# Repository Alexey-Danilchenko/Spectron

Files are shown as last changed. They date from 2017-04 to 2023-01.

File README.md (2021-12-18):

# Spectron

Spectron - an open source project for measuring and obtaining digital devices spectral sensitivity curves

Copyright (C) 2014-Now [Alexey Danilchenko](mailto:alexey.danilchenko@gmail.com), [Iliah Borg](mailto:iliah.i.borg@gmail.com)

*This is a work in progress*

# Introduction

This is the second generation of the open source Spectron project.  Initially this was conceived with the goal of constructing an automated device with an aid to accurately measure spectral sensitivity curves for digital camera sensors. The project has a broader use though and can be used to measure spectral sensitivity curves of various light sensitive sensors (not just camera sensors) - for example spectral sensitivity curves of photodiodes.

The main goal however is still to aid measurement of spectral sensitivity of digital cameras sensors and this is what this project and documentation will be aimed towards. For more details on the application of that and the ultimate reasons _why_ please [read this](CameraSRF.md).

The second generation of Spectron board was produced with the more accurate spectral readings in mind, better analogue circuitry to drive Hamamatsu spectrometers and more stable measurement results.

# Concept

The spectral sensitivity measurements of a selected device are fairly simple in principle:

1. broadband light source of high intensity is passed via monochromator
2. monochromator output is fed to the integrating sphere 
3. integrating sphere output is simultaneously captured by target device and measured spectrally
4. steps 1-3 repeated through selected spectral range in discrete steps (5nm steps over 380-720nm range for example)
5. the results of measurements from target device are scaled accodringly to the spectra of the light measured at each step and target spectral sensitivity curves are produced

# Hardware

The hardware for the above concept consists of the light source (LED or pulsed  Xenon), Mini-Chrom MC1-02 monochromator, 2.5" integrating sphere and several distinct components. The Spectrometer component is a hardware driving Hamamatsu [C12666MA](http://www.hamamatsu.com/jp/en/C12666MA.html) or [C12880MA](http://www.hamamatsu.com/jp/en/C12880MA.html) spectrometer sensor to capture spectral readings from the integrating sphere and initiate synchronised readings from target device. The Stepper Motors component is a hardware for automating monochromator operation (esentially converting manually controlled monochromator to scanning monochromator, turning broadband light source into tunable source). The Light Source component is a hardware for controlling broadband light source that provides input for the monochromator.

With the precise intensity control of the LED light source, the whole system is essentially providing tunable monochromatic light source covering the entire visible range.

All hardware component boards use [Particle Photon controllers](https://docs.particle.io/datasheets/wi-fi/photon-datasheet/) at their core to drive the functionality. Overall application control is performed from Windows/Mac application running on a computer operating the boards via Particle or local cloud (the latter is more responsive).

Boards used for all individual components can be of course utilised for standalone projects - see corresponding sections for details.

For more details please refer to individual parts of the project below:

* [Firmware](firmware) - [Particle Photon](https://www.particle.io/products/hardware/photon-wifi-dev-kit) code running on the boards
* [Hardware](hardware) - boards, schematics (Eagle) and BOM 
* [Software](software) - Windows/MacOS X application controlling the overall functionality

# Open Source

This project is open source software and hardware and is released under:

* [GNU General Public License v3](https://www.gnu.org/licenses/gpl-3.0.en.html) for the software parts and 
* [CERN Open Hardware Licence]( http://www.ohwr.org/attachments/735/CERNOHLv1_1.txt) for hardware parts

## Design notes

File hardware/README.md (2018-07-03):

# Hardware

All the custom made circuits and boards were designed in [Cadsoft Eagle](http://www.autodesk.com/products/eagle/overview). All components for these were separated into standalone Eagle library for easier access. 

__Note:__ All the boards were tuned up for making with [OSH Park](https://oshpark.com/) - all relevant DRC and ERC rule checks were therefore applied an validated.

This project has the following several distinct and standalone components:

* [Spectrometer](Spectrometer) - board controlling spectrometer and performing spectral measurements
* [Stepper Motor Control](Motor) - board driving stepper motor for automating monochromator operation
* [Light Sources](Light_Source) - selection of controllable light sources providing input for monochromator

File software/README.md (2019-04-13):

# Software

*Whilst the Spectron software is being developed and not available yet, I am releasing sample Spectrometer Application here*. 

The SpectrometerApp can operate Spectron board with Hamamatsu C12666 or C12880 sensors remotely via Particle cloud and fully control the Spectrometer operational parameters. The application exercise all Spectrometer board functionality including automatic exposure methods.

The SpectrometerApp allows to use, control and setup the following properties of the Hamamatsu spectrometers:

* Full set of parameters affecting measurement (ADC reference, gain)
* Automatic measurement
* Calculation of CCT, x, y colour metrics for emissive measurements
* Setting/limiting spectrometer range
* Calibration of saturation voltages
* Calibration of black levels
* Correction of spectral response curve

Sample screenshots:

Calibration page for Hamamatsu C12666MA spectrometer with spectral response normalisation curve:

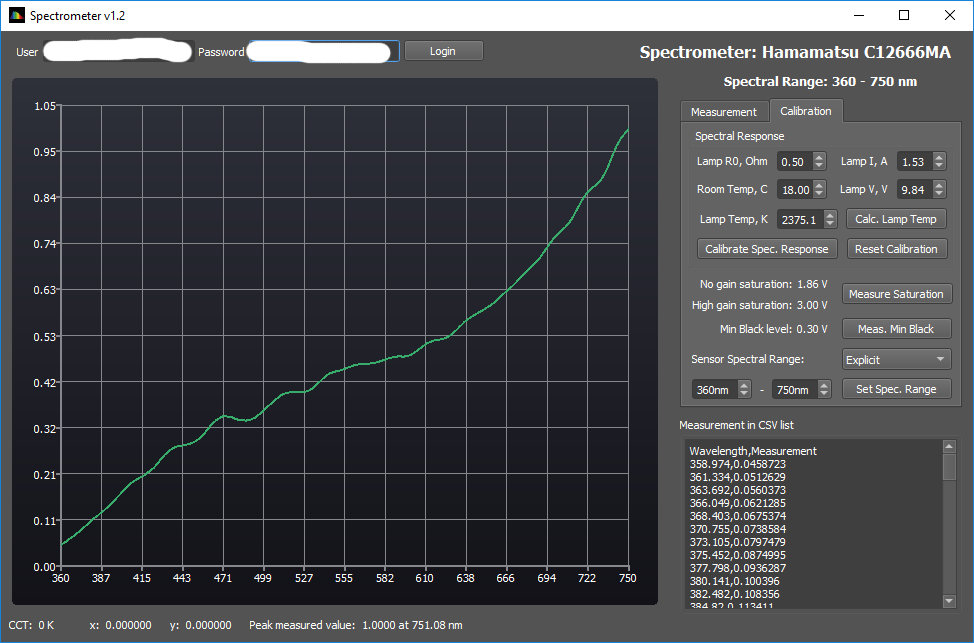
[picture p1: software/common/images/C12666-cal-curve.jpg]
C1266-Cal
 

Automatic measurement of the incandescent lamp (spectrally normalised response) for Hamamatsu C12666MA spectrometer:

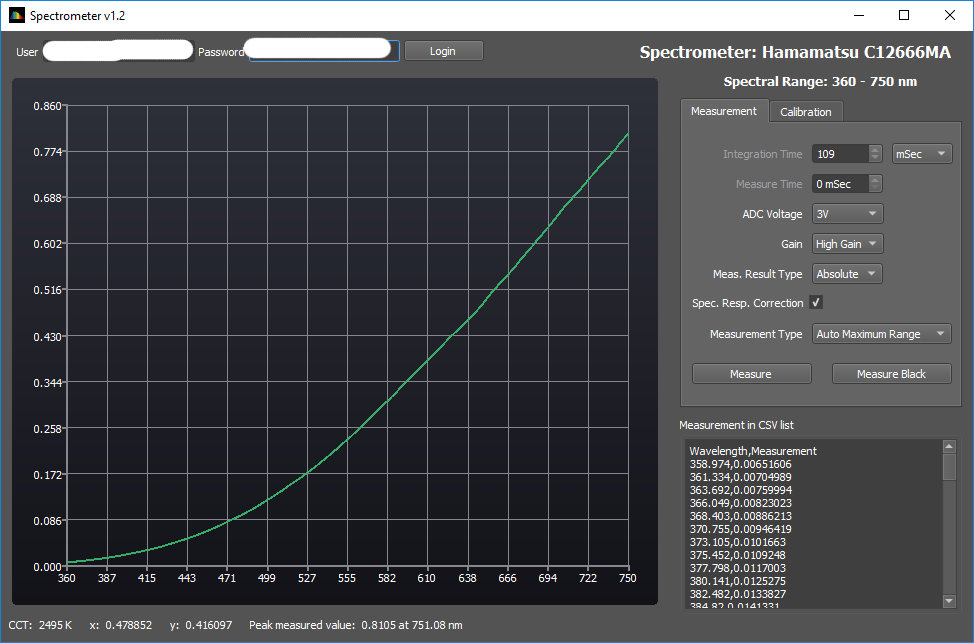
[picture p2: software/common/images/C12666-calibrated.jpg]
C1266-Cal-Meas
 

Automatic raw measurement of the incandescent lamp (no spectral normalisation applied) for Hamamatsu C12666MA spectrometer:

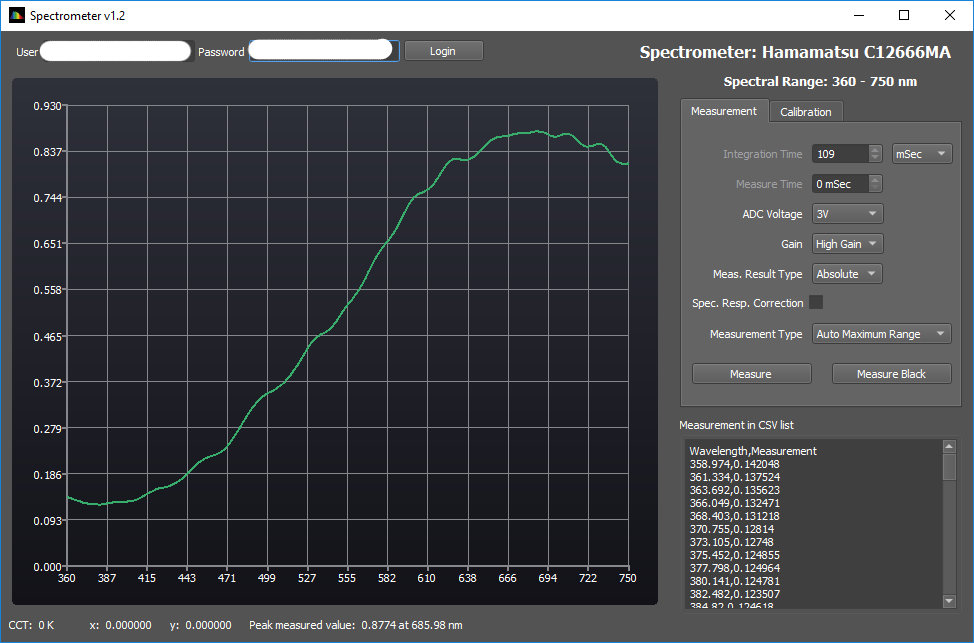
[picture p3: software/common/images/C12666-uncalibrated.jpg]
C1266-Uncal-Meas
 

The SpectrometerApp is written using QT 5.10 with project files are binaries provided for Windows 64 bit platform. It should be fairly easy to compile this on Linux or MacOS platform.

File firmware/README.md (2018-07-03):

# Firmware

This contains all the firmware (and extra example) running on the hardware boards used in this project.

All main board components (Hamamatsu [C12666MA](http://www.hamamatsu.com/jp/en/C12666MA.html), [C12880MA](http://www.hamamatsu.com/jp/en/C12880MA.html) and [TI DRV8884](http://www.ti.com/product/DRV8884)) are implemented as standalone driver objects. This makes it easier to some degree to re-use them on other Particle Photon based projects.

# Spectron 2 Board Fimwares

The main components of the boards are Hamamatsu [C12666MA](http://www.hamamatsu.com/jp/en/C12666MA.html) or [C12880MA](http://www.hamamatsu.com/jp/en/C12880MA.html) spectrometers. Whilst these spectrometer sensors share a lot of common features, operationally they are quite different. A separate firmwares therefore were produced for each spectrometer type.

The spectrometers are driven by hardware timer clock in both cases. The spectrometers readouts are performed via external 16bit SPI based ADC. The board also has four selectable precision voltage references (2.5V, 3.0V, 4.096V and 5V) to allow more precise ADC range fitting to the spectrometer output.

For the purpose of the measurements, the board provides two external trigger pins (only one can be selected and used at a time). The spectrometer driver makes use of the selected trigger pin at the time of the measurement (the trigger signal can be offset and issued prior to the measurement with configurable delay). For the goals of this project, these pins are labelled `TRG_FLASH` and `TRG_CAMERA` in the code for flash and digital camera triggering accordingly.

The spectrometer drivers also have configurable black subtraction mode that could be used to eliminate spectrometer offset voltage (that appears to be nonlinear). This can be configured in one of the following ways:

- to capture black frame output manually 
- to capture black frame output before the main measurement
- to capture black frame output after the main measurement

When black levels are captured the spectrometer readings are adjusted accordingly.

The selected reference voltage, gain (if supported) and black mode are stored in EEPROM and persist even when the board is powered off.

Calibration data provided by Hamamatsu for each sensor (used to determine wavelengths mapping for each sensor) needs to be provided to the driver to get accurate readings. If omitted, the calibration data from my own sensors is used as a fall-back.

All the readings are captured as floating point values in 0..1 range. By default, readings from the driver are also bandpass corrected (this is configurable) using Stearns and Stearns (1988) bandpass correction method.

Below are individual specifics of each firmware.

## Spectron 2 - С12666MA firmware

[This firmware](Spectron_12666) implements the functionality for the Spectron2 board with Hamamatsu [C12666MA](http://www.hamamatsu.com/jp/en/C12666MA.html) spectrometer connected (using appropriate sensor board). 

The spectrometer is driven by hardware clock with 100KHz (default) or 59KHz frequency. In both modes sensor readouts are oversampled to provide more stable readings. The slower clock is enabled by uncommenting `ADC_AVG_4` definition. The specifics of each clock frequency:

* 100KHz: integration times: 11.3msec - 10sec, oversampling with two averaging reads per spectrometer pixel

* 59KHz: integration times: 18.51msec - 10sec, oversampling with four averaging reads per spectrometer pixel

In addition to selectable voltage references, the firmware can enable/disable spectrometer supported gain. This may allow even tighter usage of ADC range.

The firmware is implemented partially outside of Particle Photon HAL - using direct hardware and ports access for performance critical parts (timer, soft pin interrupts, ADC readouts). The readouts are triggered by software pin interrupt - C12666MA (unlike C12880MA) lacks hardware support for signal ready trigger.

## Spectron 2 - С12880MA firmware

[This firmware](Spectron_12880) implements the functionality for the Spectron2 board with Hamamatsu [C12880MA](http://www.hamamatsu.com/jp/en/C12880MA.html) spectrometer connected (using appropriate sensor board). 

The spectrometer is driven by hardware clock with 156KHz (default) or 200KHz frequency. In 156KHz frequency mode sensor readouts are oversampled to provide more stable and smoother readings. The specifics of each clock frequency mode:

* 100KHz: enabled by setting `SPEC_CLK_TICK_TIMER` definition to `SPEC_CLK_156KHZ`, integration times: 345.6usec - 1sec, oversampling with two averaging reads per spectrometer pixel, produces much smoother output, works well even though it is below minimal Hamamatsu specified working frequency

* 200KHz: enabled by setting `SPEC_CLK_TICK_TIMER` definition to `SPEC_CLK_200KHZ`, integration times: 270usec - 1sec, no oversampling with single read per spectrometer pixel, minimal official working frequency for C12880MA according to Hamamatsu specification

The C12880MA does not support gain but is a lot more sensitive than C12666MA. Using selectable reference voltages will allow better use of ADC range.

The firmware is implemented substantially outside of Particle Photon HAL - using direct hardware and ports access for performance critical parts (GPIO pin access, timer, pin interrupts, ADC readouts). The readouts are triggered by C12880MA hardware TRG pin which allows more reliable read timings.

## Spectron 2 - LCD demo firmware

[This firmware](LCD) demonstrates usage of the Spectron 2 board with Hamamatsu C12666MA spectrometer and multipurpose interface connector with [Adafruit 2.2" 18-bit TFT LCD module](https://www.adafruit.com/product/1480) attached. The C12666MA driver should be taken from [C12666 firmware](Spectron_12666) (this avoid the duplication). The firmware will wait for trigger pin (button attached to it) to be risen high, start spectral measurement of predefined integration time and display the spectrum on the TFT screen afterwards.

This code was tested on early stages of the project development but is not actively maintained. Its main purpose if to provide a demonstration of Spectron 2 board capabilities.

# Motor Board Firmware

[This firmware](Motors) implements functionality for the Spectron 2 Motors board that is operating stepper motor and rotary encoder to control monochromator wavelength selection. The [TI DRV8884](http://www.ti.com/product/DRV8884) is used to drive stepper motor and [LS7083](http://www.omnipro.net/lsi-csi/LS7083-S) quadrature converter chip to interface with rotary encoder. 

The DRV8884 allows to fine tune stepper parameters to suit each and every application. All of these stepper parameters as well as position details are stored in EEPROM and persist even when the board is powered off. The expectations are that these particular boards will be tuned up (for example using Particle cloud functions via Particle console) for a specific application and all the board parameters will be set up and stored at that stage.

The firmware is designed to operate in terms of target device position and its lower and upper limits. The logical po
sition is mapped into physical steps for controlling stepper. All position parameters (current position, lower and upper position limits) are also persisted in the EEPROM. For this specific application, current position reflects wavelength selected on monochromator with upper and lower limits designating the spectral range that monochromator can control.

# LED Light Source

[This firmware](LED) implements functionality for Spectron 2 LED Lightsource board using [Yuji VTC 5600K wide spectrum LEDs](https://store.yujiintl.com/collections/vtc-series/products/vtc-series-high-cri-cob-led-135l-pack-5-pcs?variant=45426214099). 

The firmware allows controlling the output brigntness of two LED channels independently (each channel up to 4095 brightness levels) or simultaneously, enabling/disabling LED output as well as doing timed exposures.

It is used as a main light source for Spectron 2 project. 

# Pulsed Xenon Light Source

[This firmware](Xenon) implements functionality for Spectron 2 Xenon Lightsource board using [Excelitas FX-116x series lamps](http://www.excelitas.com/Pages/Product/1100-Series-Family.aspx) on [Excelitas/Perkin-Elmer trigger module FYD‐1150‐B](http://www.excelitas.com/Downloads/DTS_1100Series_Trigger_Modules.pdf) driven by [Excelitas/Perkin-Elmer PS-11xx power supply](http://www.excelitas.com/Downloads/DTS_1100Series_Power_Supplies.pdf). 

The firmware allows controlling the output brigntness (average output power) of the flash lamp, or varying voltage or trigger rate directly (within allowed lamp  specifications), enabling/disabling Xenon Lamp output as well as doing timed exposures.

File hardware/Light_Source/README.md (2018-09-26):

# Light Sources

The Spectron 2 project uses a wideband light source component as an input to the monochromator. Several light sources with full visible spectrum coverage were evaluated, built and tested for this project. It is important to realize that flat spectrum is not necessary in this application. What is required from a light source is continuous spectrum, with no gaps. Evaluated light sources are all satisfy this criteria. Below is the list of the light sources chosen as a result of this evaluation:

* [LED light source](LEDs). _Pros_: great stability and very flexible brightness control, very compact solution electronically. _Cons_: difficult optical constructs required to blend light output from several LEDs into uniform shape suitable as an input for monochromator.

* [Pulsed Xenon short arc light source](Xenon). _Pros_: great visible spectrum coverage, much more even response across spectrum than any other light source solution, compact package and point light source best suited to guide light into the monochromator (very simple construct - essentially lamp against monochromator entrance). _Cons_: expensive if bought from the source (although could be found on eBay at bargain prices), bulky electronics dealing with high voltage triggering (power supplies and trigger modules).

* Tungsten halogen light with regulated power source. _Pros_: the cheapest and readily available solution. _Cons_: needs substantial cooling, needs collimating optics or fiber optical guide to input monochromator, spectrum is the least balanced of all the above solutions (the blue range of the spectrum is weakest), readily available solutions are bulky and external. *NOTE*: This was also tested as readily available light source with fiber optical guide to monochromator and works fine. It is not however considered in details here and mentioned purely due to being very cost effective alternative to the other light sources.

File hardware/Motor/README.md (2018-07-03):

# Motor controller - programmable to scan of a range of wavelengths

This is the board that is responsible for monochromator automation. The board is capable of driving single stepper motor and receiving input from rotary encoder to help with position verification. The board requires minimum +12V DC power supply to operate. The board is also quite useful as standalone Particle Photon stepper driver.

Board schematic is also [available as standalone PDF](Motors.pdf). Bill of material [is available in Excel format](Motors_BOM.xlsx).

The following are the board layouts available (generated by OSH Park preview):

* Spectron 2 Motors - front and back

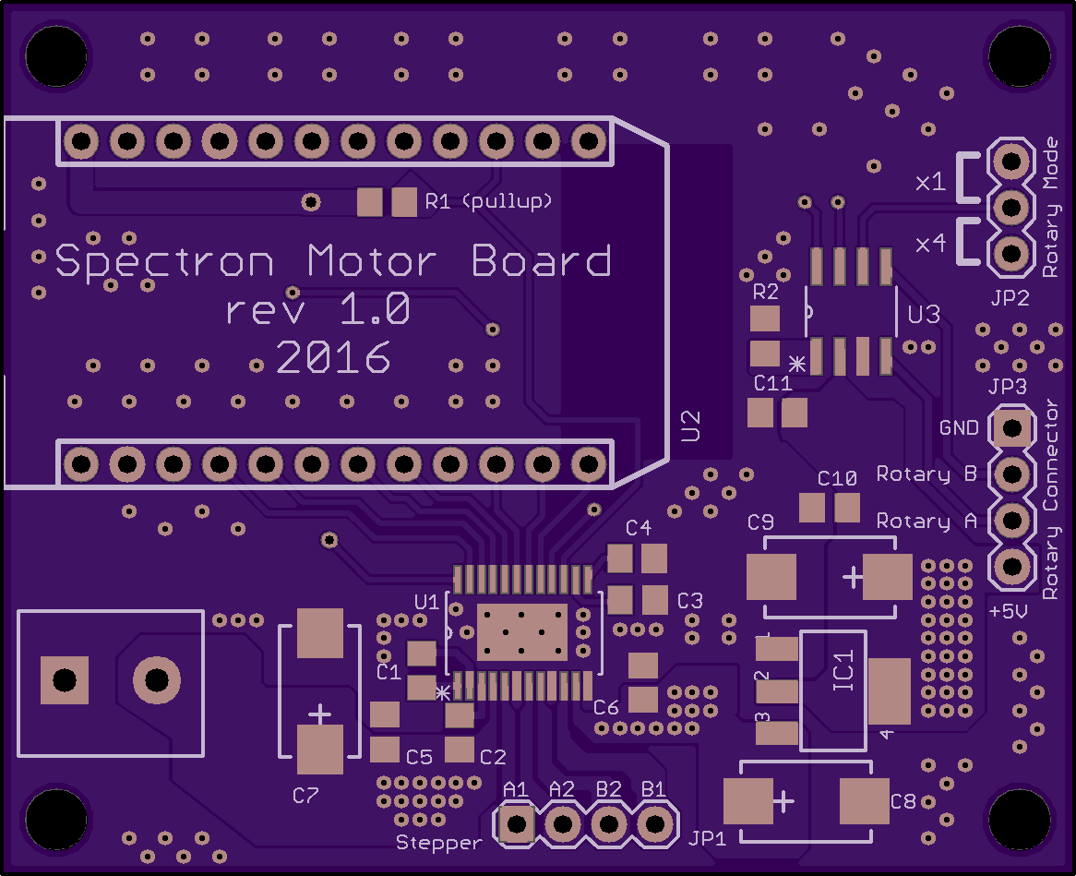
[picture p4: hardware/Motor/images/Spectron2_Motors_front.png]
MOTF
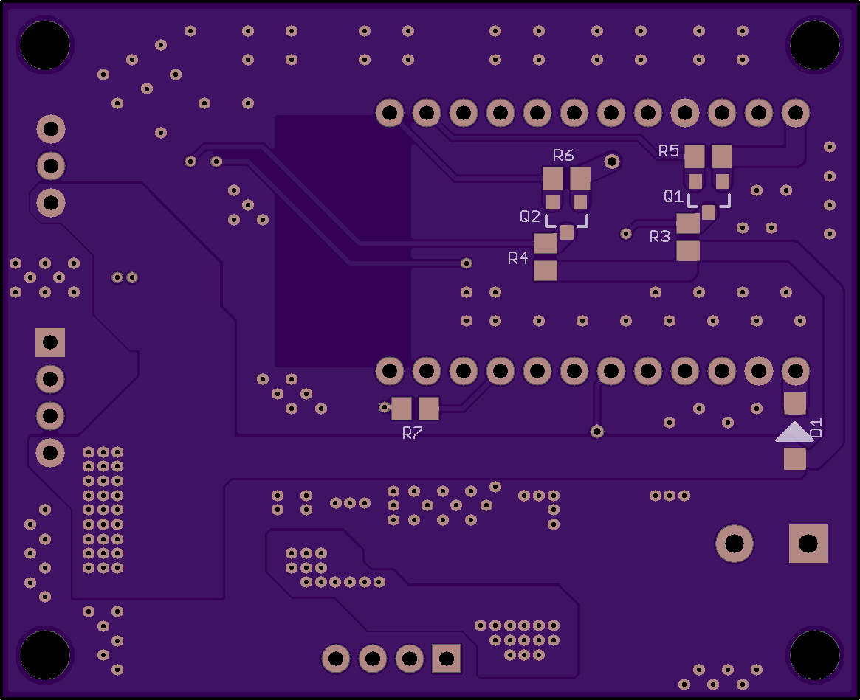
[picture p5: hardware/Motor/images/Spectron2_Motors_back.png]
MOTB


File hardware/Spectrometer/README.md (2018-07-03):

# Spectron 2 - Spectrometer controlling board

This is the main board that is responsible for spectral measurements. The board has analogue circuitry to drive Hamamatsu [C12666MA](http://www.hamamatsu.com/jp/en/C12666MA.html) or [C12880MA](http://www.hamamatsu.com/jp/en/C12880MA.html) micro spectrometers and interfaces to trigger external devices or light sources simultaneously with measurements. The board requires +5V DC power supply to operate.

The board also has a multipurpouse interface connector suitable for custom adaptations that provides access to SPI, I2C and generic digital/analogue pins on Particle Photon. This project does not make use of this connector but example firmware is provided to demonstrate its use with Adafruit 2.2" 18-bit TFT LCD module.

Board schematic is also [available as standalone PDF](Spectron2.pdf). Bill of material [is available in Excel format](Spectron2_BOM.xlsx).

The Hamamatsu C12666MA and C12880MA spectrometers have different hardware pinout and for that reason they are attached to this board through their own little sensor boards. Those were designed with my specific attachment to integrating sphere in mind and come in both vertical and horisontal layouts (they differ in a way the main board attaches to the sensor board).

The following are the board layouts available (generated by OSH Park preview):

* Spectron 2 - front and back

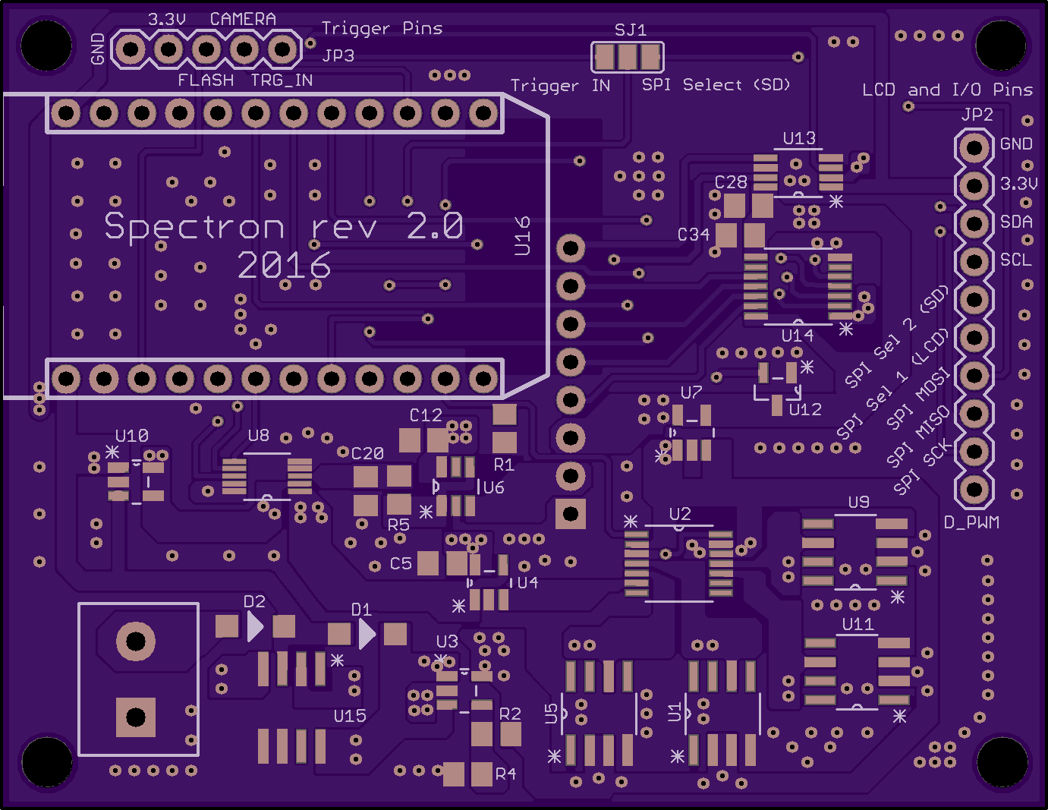
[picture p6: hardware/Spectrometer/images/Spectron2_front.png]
SF
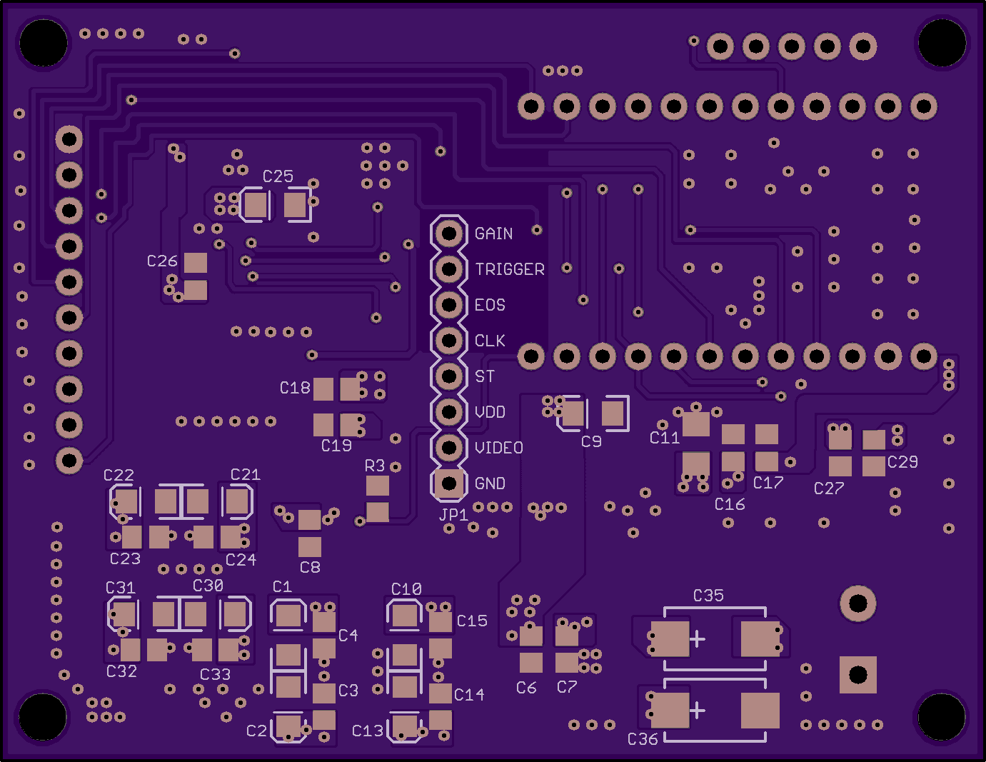
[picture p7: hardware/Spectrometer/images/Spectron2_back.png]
SB
 

* Hamamatsu C12666 sensor board (horisontal) - front and back

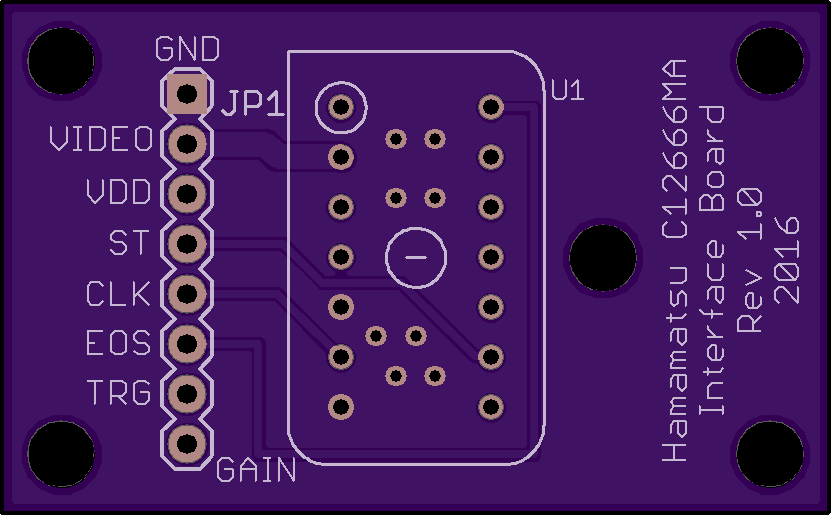
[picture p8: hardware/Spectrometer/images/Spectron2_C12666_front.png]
SF1266
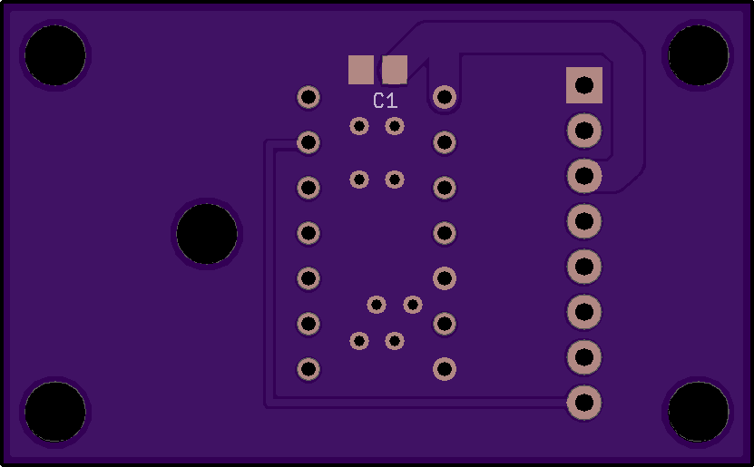
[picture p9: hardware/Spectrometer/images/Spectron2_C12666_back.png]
SB1266
 

* Hamamatsu C12666 sensor board (vertical) - front and back

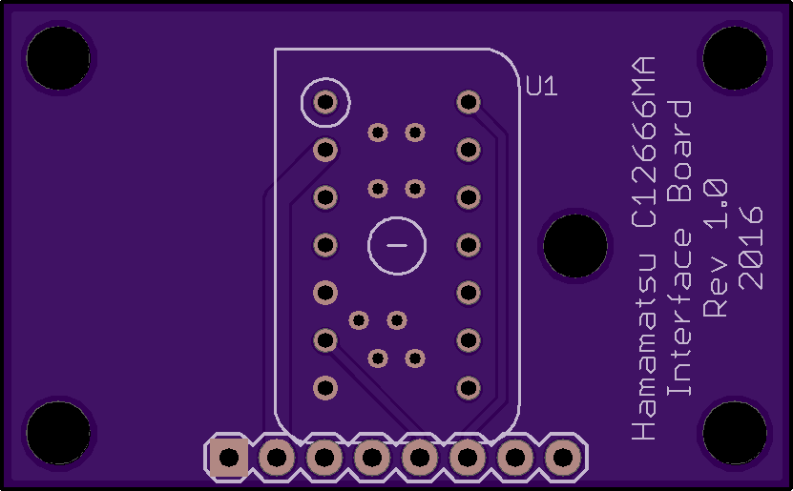
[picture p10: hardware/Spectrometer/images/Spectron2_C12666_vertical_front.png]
SFV1266
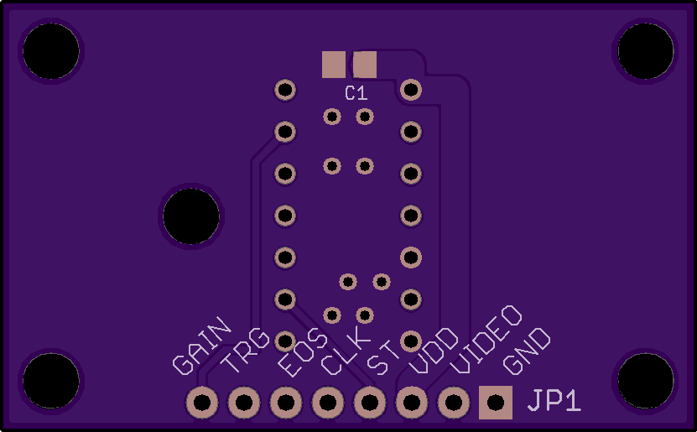
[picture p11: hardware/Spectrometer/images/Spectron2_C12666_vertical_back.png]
SBV1266
 

* Hamamatsu C12880 sensor board (horisontal) - front and back

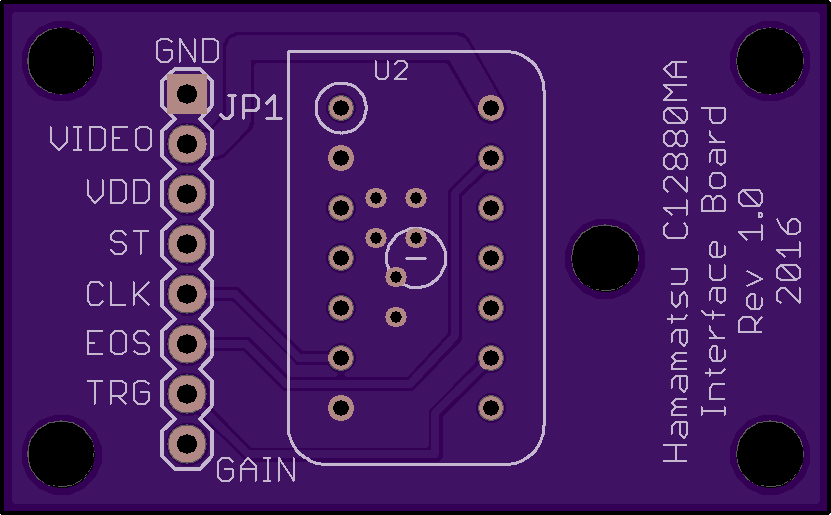
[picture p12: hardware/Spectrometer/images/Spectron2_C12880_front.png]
SF1288
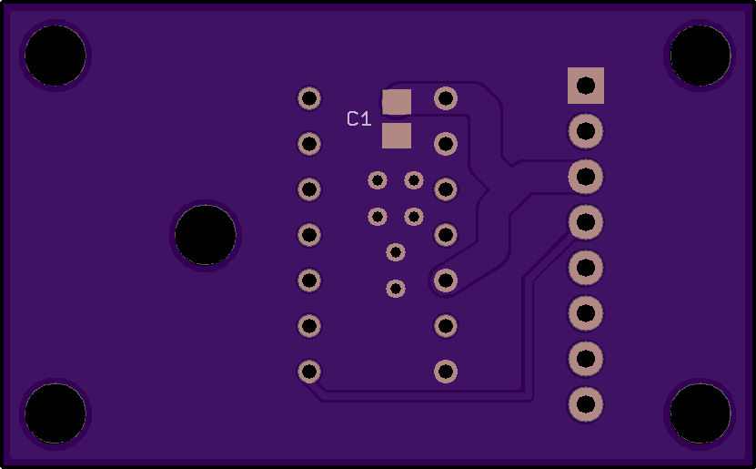
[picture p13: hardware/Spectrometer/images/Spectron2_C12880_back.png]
SB1288
 

* Hamamatsu C12880 sensor board (vertical) - front and back

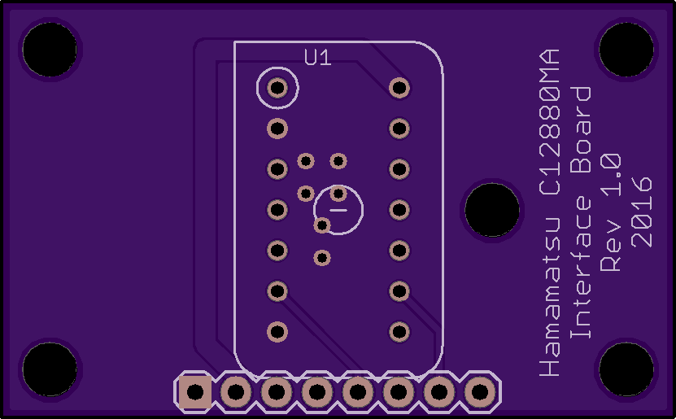
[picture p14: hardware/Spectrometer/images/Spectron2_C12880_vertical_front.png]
SFV1288
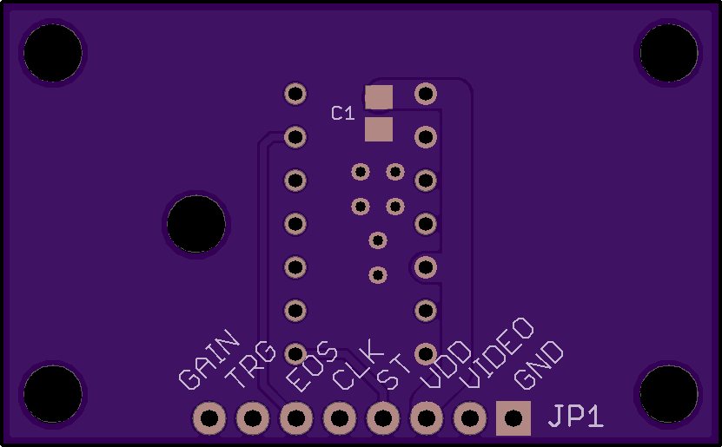
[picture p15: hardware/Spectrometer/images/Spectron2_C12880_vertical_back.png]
SBV1288


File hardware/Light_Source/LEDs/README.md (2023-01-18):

# LED Light Source

The LED light source component uses [Yuji LEDs](https://store.yujiintl.com/). More specifically their VTC (CRI 98) LEDs in [COB package for 5600K](YJWJ040-1.0_YJ-VTC-135L-G01.pdf) correlated colour temperature. A package of 4xVTC LED COBs clustered together is used for this light source. For more technical details on individual COB specifications see [Yuji LED web store](https://store.yujiintl.com/collections/led-cobs/products/yujileds-cri-98-9w-cob-led-135l).

These LEDs were chosen for the broad spectrum coverage they provide. An example of spectral response captured from the LEDs used in this setup ([also available as .CSV file](VTC5600_spectrum.csv)):

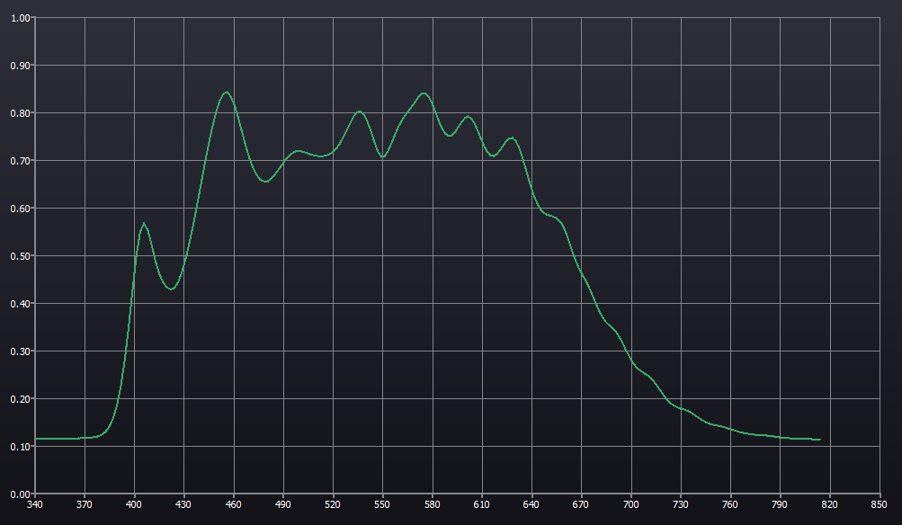
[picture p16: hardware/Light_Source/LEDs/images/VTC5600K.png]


This component consists of two distinct and connected parts - LED driver/controller board and LED light head assembly. The whole circuit requires +12V/5A DC power supply to operate.

The photo below gives a clearer idea of the asssembled setup:

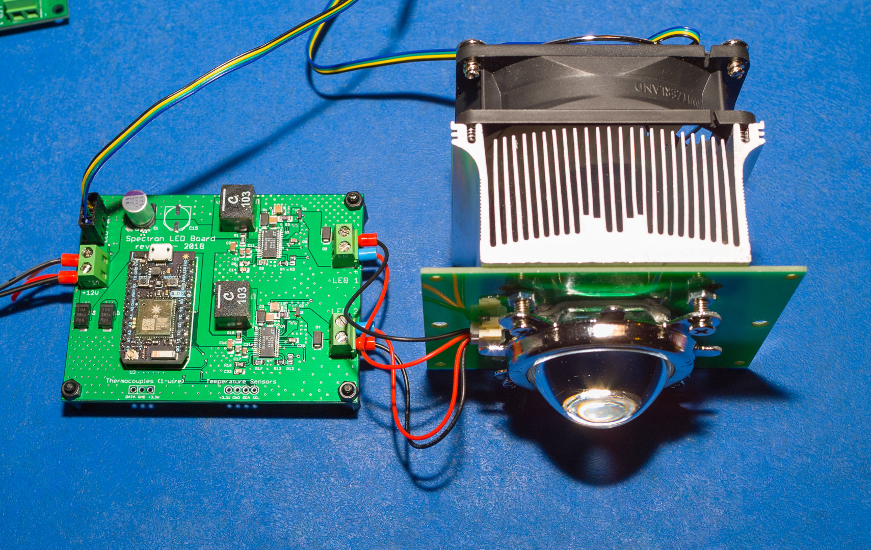
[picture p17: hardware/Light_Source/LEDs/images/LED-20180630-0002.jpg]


### LED Driver Board

The LED driver/controller board is a standalone LED driver with PWM control and 4000:1 dimming ratios (programmatically controlled). The LED driver board has two constant current channels - each capable of driving 450mA LEDs with up to 50V. This setup uses 2x LED strings (one per each channels) with 2xLEDs in series in each string (4x LEDs in total).

The board has 4 pin PWM connector allowing to control LED heatsink fan (if it is used). It also features I2C temperature sensor connector for board/environment temperature monitoring (if used) and 1-Wire thermocouple interface connector for LED temperature monitoring (if used).

Board schematic is also [available as standalone PDF](LED.pdf). Bill of material [is available in Excel format](LED_BOM.xlsx).

The following are the board layouts available (generated by OSH Park preview):

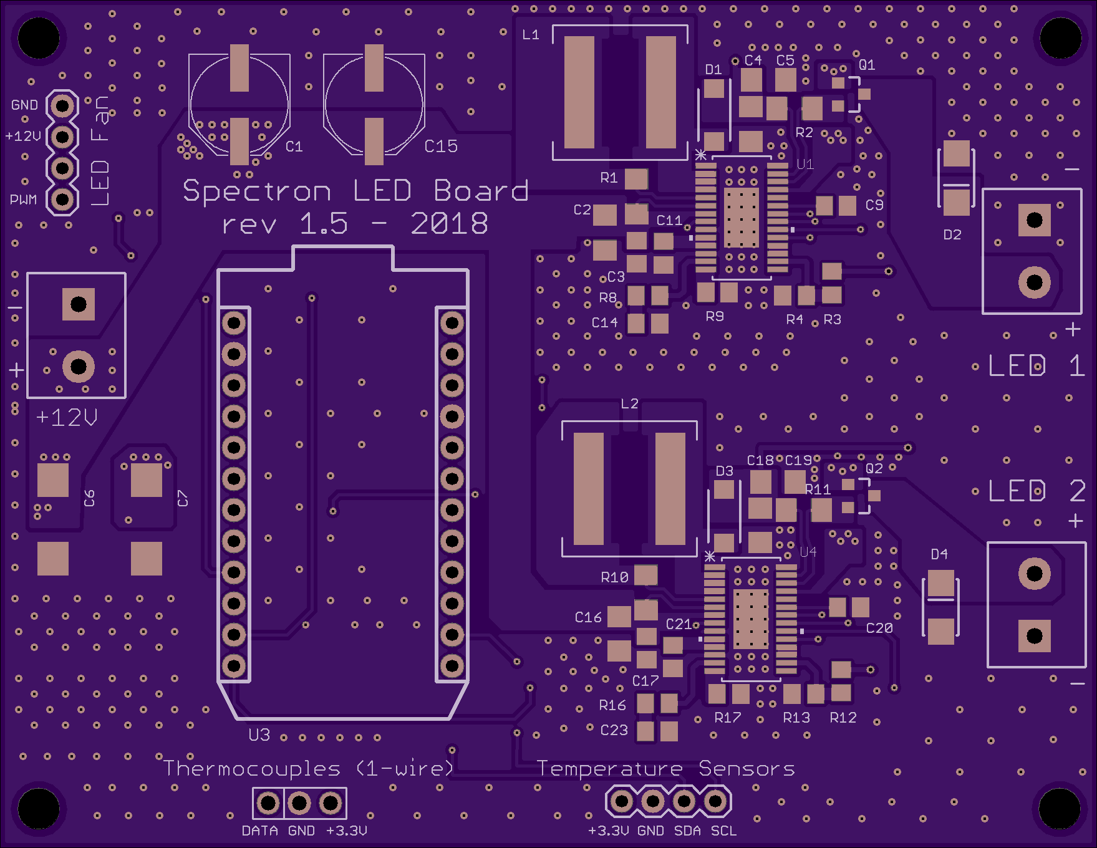
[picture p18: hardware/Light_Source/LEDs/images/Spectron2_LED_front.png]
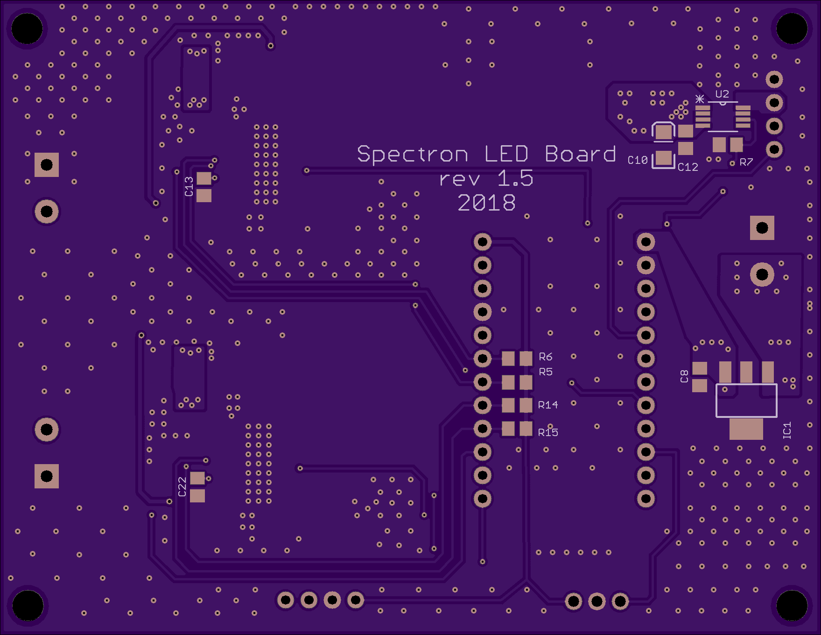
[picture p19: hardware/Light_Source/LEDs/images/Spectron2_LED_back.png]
SB
 

### LED Light Head Assembly

This assembly utilises the board with connector to the main LED driver board and mechanical connectors to 4xVTC LED COBs mounted directly on heatsink. The board has square cutout that fits tightly around 2x2 layout of VTC LED COBs with metallic pins soldered to the board acting as mechanical connectors to the LEDs. This allows to keep LEDs and heatsink setup separate from the board and optical assembly for easier replacement of the parts. The LED COBs are connected in series of two per string. 

The LED COBs are glued to a heatsink directly with [Arctic Silver Thermal Adhesive](http://www.arcticsilver.com/arctic_silver_thermal_adhesive.htm) in a tightly formed cluster. In series connection for each pair is formed by direct wire soldering onto the LEDs. This photo illustrates the setup:

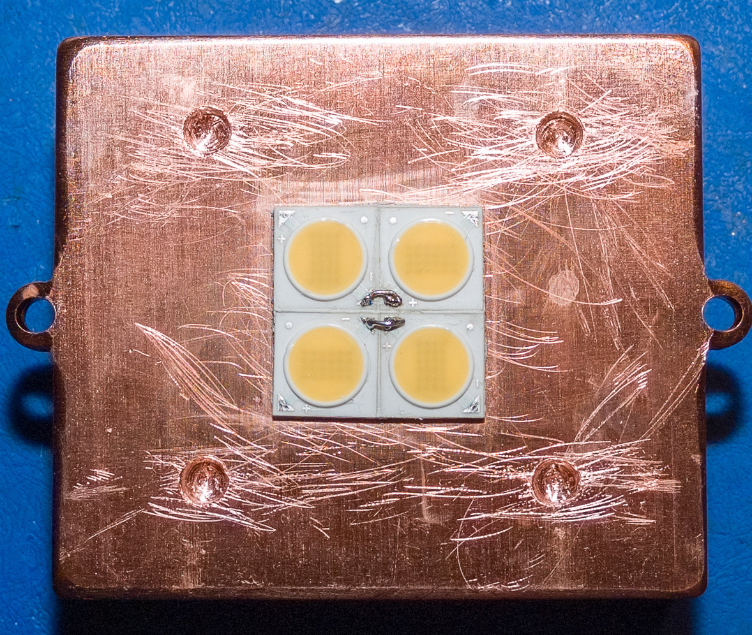
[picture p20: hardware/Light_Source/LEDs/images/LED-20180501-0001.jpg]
 

The board with soldered pins on top of LEDs mounted on heatsink as follows:

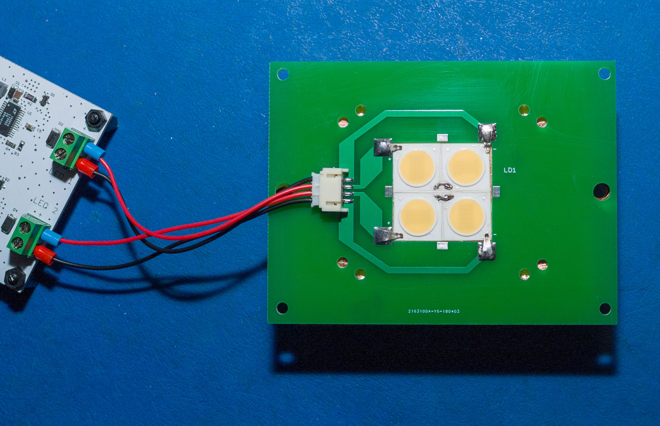
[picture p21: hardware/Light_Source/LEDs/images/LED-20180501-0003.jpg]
 

The board then has a range of holes to allow attachments of the reflector, condenser lens and holder. Below is the example of the fully assembled setup:

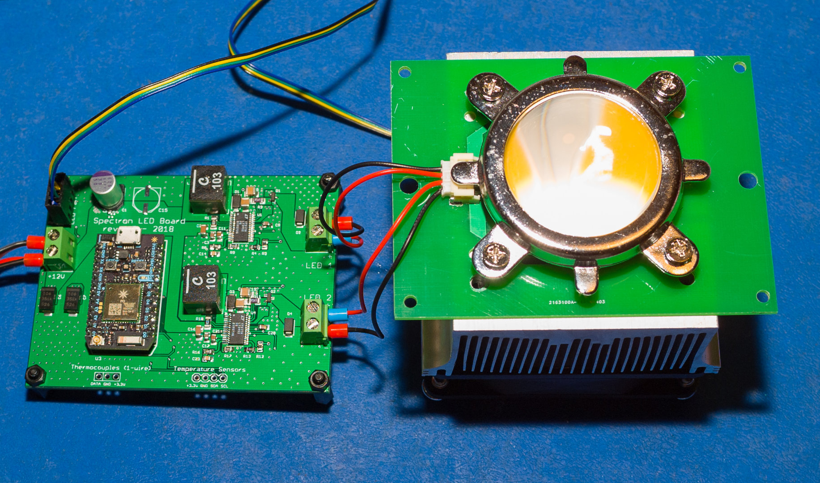
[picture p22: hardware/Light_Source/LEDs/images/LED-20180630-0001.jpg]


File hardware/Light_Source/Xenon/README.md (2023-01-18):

# Xenon Light Source

The Xenon light source component utilises compact pulsed guided short arc Xenon lamp with build in reflector. There are several manufacturers of those lamps - [Hamamatsu](https://www.hamamatsu.com/jp/en/product/light-and-radiation-sources/lamp/xe-f.html) and [Excelitas/Perkin-Elmer](https://www.excelitas.com/product/1100-series-short-arc-xenon-lamps) are well known for their expertise in this area. The setup built and tested for the Spectron 2 utilises [Excelitas/Perkin-Elmer](http://www.excelitas.com/) lamps simply because the off-the-shelf components for them are much easier to find reasonably priced on second hand market (eBay is a great source for them).

This light source construction makes it a very efficient light source for monochromator with very little light loss even without special complicated collimating optics. The metal can lamps from the families referenced above also allow to exceed to a certain degree rated power parameters when lamp is mounted on cooling jackets with sufficient thermal mass. This was tested and fully exploited in firmware accompanying this light sources to provide more efficient light output.

This light source uses [Excelitas/Perkin-Elmer FX-1160 (arc length 1.5mm) or FX-1163 (arc length 3mm) lamps](hhttps://www.excelitas.com/product/1100-series-short-arc-xenon-lamps) widely available new on [eBay at reasonable prices](https://www.ebay.com/itm/Excelitas-FX-1163RT-High-Output-Short-Arc-Xenon-Flashlamp-Flashtube-New-in-Box/122220610629). The lamp also needs a corresponding high voltage (400-1000V) power supply and high voltage trigger module. In our case the [Excelitas/Perkin-Elmer PS-1120 high voltage power supply](http://www.excelitas.com/Downloads/DTS_1100Series_Power_Supplies.pdf) was used together with [Excelitas/Perkin-Elmer FYD‐1150‐B high voltage trigger module](http://www.excelitas.com/Downloads/DTS_1100Series_Trigger_Modules.pdf). The controller board was made to allow to programmatically control the output voltage and triggering rate.

The whole light source component requires external +24V/3A DC power supply to operate.

The pictures below give a clearer idea of the asssembled setup for this component with the lamp triggering:

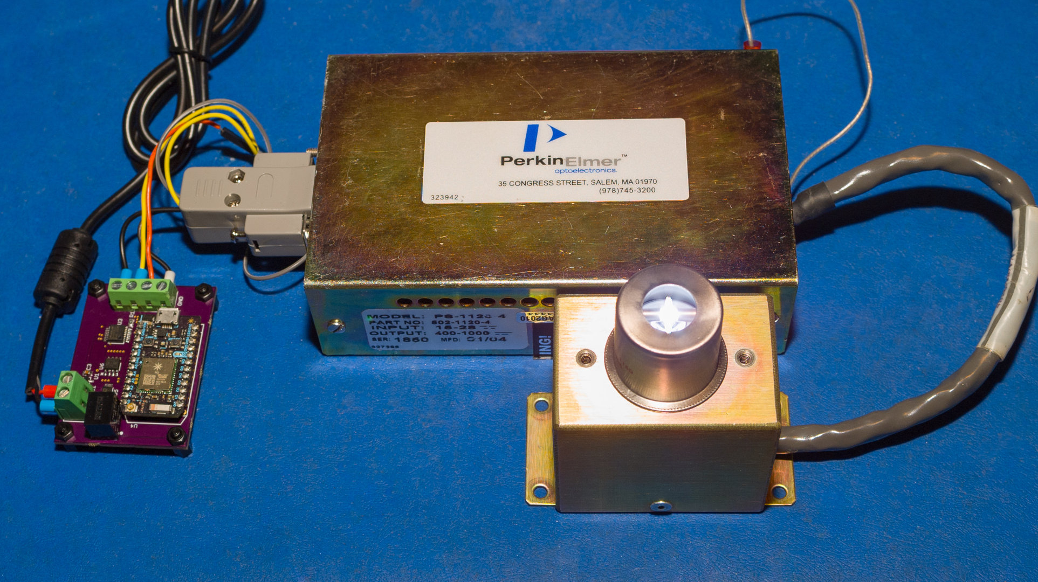
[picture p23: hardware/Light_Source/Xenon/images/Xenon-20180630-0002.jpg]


The controller board uses 0-10V DAC to set output voltage of the high voltage power supply - these power supplies tend to use voltage reference of 1/100th of the desired output to control the output voltage. The board has 2 pin connector to the exnternal +24V DC power supply and 4 pin connector to the high voltage power supply driving the lamp. The output 4 pin connector provides +24V DC, non-isolated logic level trigger signal and 0-10V voltage reference. The [Excelitas/Perkin-Elmer PS-1120 high voltage power supply](http://www.excelitas.com/Downloads/DTS_1100Series_Power_Supplies.pdf) used here has isolated trigger input so no extra isolation is needed. However external trigger signal isolation may be needed (via optocoupler) if a different high voltage power supply is used.

Board schematic is also [available as standalone PDF](Xenon_Light.pdf). Bill of material [is available in Excel format](Xenon_Light_BOM.xlsx).

The following are the board layouts available (generated by OSH Park preview):

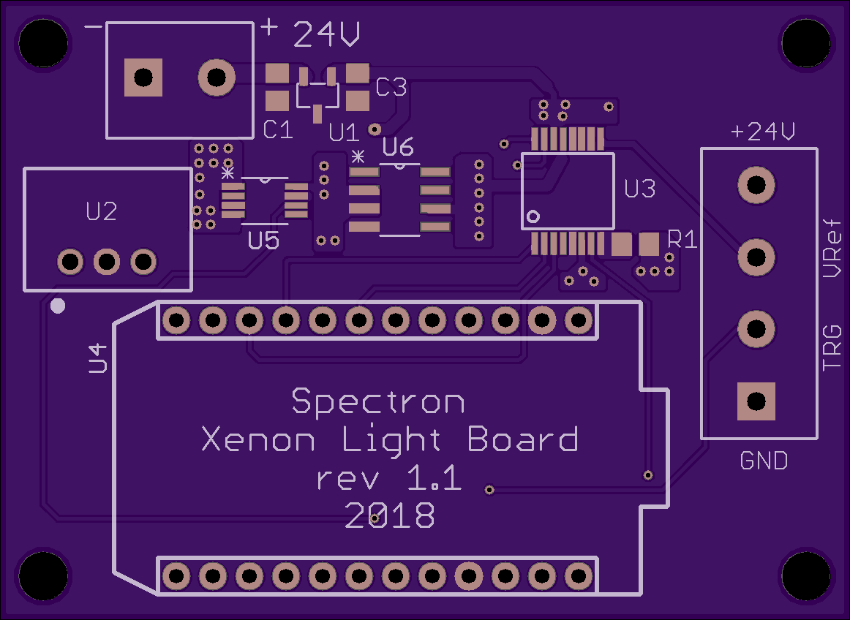
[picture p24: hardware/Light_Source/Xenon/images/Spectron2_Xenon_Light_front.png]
 SB

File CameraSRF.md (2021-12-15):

# Practical application of camera sensor spectral response function

The goal here is to obtain data that would allow us to compute an ad hoc (flexible, actual scene- and light-tailored, adjustable during the raw conversion process) colour transform between raw RGB and perceived colour, based directly on the spectral properties of the light in the scene and the sensor spectral sensitivity.

The popular approach to camera colour profiling is to shoot a target, and, knowing the colours on the target, to compute a transform between those colours and the corresponding values in the digital capture.

Problems with the profiling that is based on shooting a target include:
- minimizing illumination non-uniformity across the target (in terms of intensity / white balance)
- minimizing stray light
- minimizing (colour) reflexes from the surroundings
- minimizing flare and glare introduced by the lighting and the lens
- minimizing lens vignetting
- minimizing digital vignetting / angular dependencies introduced by the sensor
- optimizing exposure to avoid noisy and non-linear areas on the sensor characteristic curves
- minimizing the target reference data uncertainty
- a limited number of patches on the target, and the limited real-world-adequacy of those patches’ spectral distributions
- dependency of the resulting profile on the shooting light spectrum is very problematic, given the diversity of the light sources used for actual shooting
- limited quality and accuracy of chromatic adaptation in a 3D colour domain when attempting to adapt the profile to the light in an actual shot (especially when the actual light sources don't have smooth spectra, like it is with LEDs and fluorescent light sources, or, in general, when the light used to shoot the target and the light in the actual shot are far apart spectrally / CCT-wise)

In summary, profiling based on shooting a target has rather limited applicability as it depends on many factors, some of which are hard / costly to control, while some, mostly the chromatic adaptation, may not be solvable at all.

To overcome these limitations we will be using the basic physical property of the sensor - spectral sensitivity (it has, by the way, its own EXIF tag, 34852 / 0x8824, which we never saw to be used). Spectral sensitivity, measured once, can be used to create colour transforms without any target shots, on the fly, and those transforms can be tailored to the light in an actual shot.

## Terminology

**SPD** - _spectral power distribution_, a graph / histogram (often a table) of wavelengths and corresponding intensities (energy levels). SPD characterizes emitted or reflected light. SPD of the light falling on a sensor / receptor (human eye) causes sensor / receptor excitation.

Sensor excitation results in raw RGB response in the form of raw RGB data.

Eye excitation results in the sensation of colour, that is in human colour perception. Human response can be represented as CIE XYZ. (Actually, we can use the LMS responsivity spectra of human perception instead of XYZ.)

**SRF** - _spectral response function_ (aka spectral sensitivity). Here it is used to predict the sensor raw RGB response when the sensor is excited by a light of the given wavelength falling on it.

SRF for a sensor is much like an observer colour matching functions for human perception; in both cases responses are additive, that is the total response to an SPD falling on the sensor / receptor is the sum of responses to individual pairs 'wavelength - intensity'.

We will use **\<cam observer\>** for SRFs.

## Computation method

To compute a colour transform using an SRF, first we need to define some excitation and determine both the human response (XYZ) and the camera response (raw RGB) for this excitation.

We will be using \<cam observer\> over a simulated excitation SPD in order to obtain a set of raw RGB data. Such simulation offers at least 3 benefits:
- any synthetic calibration target can be used, including targets that are nearly impossible to create physically and shoot; all one needs is spectral measurements of objects - colours in Nature (leaves, flowers, ...), various skin tones, etc. - and now there in no target properties uncertainty or need in exposure optimization;
- since the light is virtual, each synthetic calibration target "patch" is under the same light SPD (no angular dependencies, no intensity variations, no white balance variations, no shading, no colour reflexes from the surroundings, no lens / digital vignetting, etc.);
- we can calculate light-in-the-scene tailored colour transforms "on the fly" by interactively adjusting the light SPD while rendering raw, or using measured light SPD to match the light in the actual photographed scene (instead of applying chromatic adaptation on top of a colour transform or interpolating between the colour transforms in a reduced, compared to spectra, 3D colorimetric space).

### Inputs
- simulated spectral excitation - some set of spectral data that excites the receptors (the sensor and the eye). It can be a product of some reference spectral reflection data and some light SPD, or SPDs of a multitude of coloured lights / filtered lights
- sensor SRF (camera observer)
- the human perception (CIE XYZ data) of that spectral data (to be determined using the standard colorimetry formulae)
- the camera perception (raw RGB) of that spectral data (predicted trough the sensor SRF / camera observer)

### End result
- a colour transform between raw RGB and XYZ colorimetric space, can be a 3x3 matrix, can be something more complex

### Let
- *\<scene light SPD\>* be a known / asserted light in a scene for which we want to calculate the colour transform
- *\<calibration target sd\>* be spectral reflection data of a real / synthetic calibration target
- *\<human observer\>* be the observer used to render \<calibration target sd\> to XYZ

To determine the raw RGB, we will be rendering the sensor excitation through the camera observer.

XYZ (human perception) is:

> *\<calibration target XYZ\>* = *\<scene light SPD\>* * *\<calibration target sd\>* * *\<human observer\>*

From the camera side, with *\<calibration target sd\>* in \[0 .. 1\] domain

> *\<simulated sensor excitation\>* = *\<calibration target sd\>* * *\<scene light SPD\>*

By definition

> *\<sensor excitation\>* * *\<cam observer\>* = *\<raw RGB\>*

Thus

> *\<simulated raw RGB\>* = *\<simulated sensor excitation\>* * *\<cam observer\>*

Having *\<calibration target XYZ\>* and *\<simulated raw RGB\>* we can proceed to calculate a colour transform.

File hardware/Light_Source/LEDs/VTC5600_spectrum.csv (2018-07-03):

Wavelength | Measurement
325.751 | 0.0523601
328.134 | 0.119326
330.515 | 0.115091
332.895 | 0.115171
335.274 | 0.115119
337.652 | 0.115133
340.027 | 0.114955
342.402 | 0.11523
344.774 | 0.115035
347.145 | 0.114638
349.515 | 0.115063
351.882 | 0.115195
354.248 | 0.115177
356.612 | 0.115141
358.974 | 0.115152
361.334 | 0.115265
363.692 | 0.115355
366.049 | 0.11595
368.403 | 0.116141
370.755 | 0.116135
373.105 | 0.116733
375.452 | 0.118325
377.798 | 0.119781
380.141 | 0.123509
382.482 | 0.129645
384.82 | 0.140261
387.156 | 0.158131
389.49 | 0.186038
391.821 | 0.226206
394.15 | 0.280545
396.476 | 0.348927
398.8 | 0.425779
401.121 | 0.498651
403.439 | 0.549225
405.754 | 0.567
408.067 | 0.552515
410.377 | 0.521328
412.684 | 0.487716
414.989 | 0.461417
417.29 | 0.442937
419.588 | 0.43229
421.884 | 0.428162
424.176 | 0.431721
426.466 | 0.444214
428.752 | 0.465883
431.036 | 0.494465
433.316 | 0.528558
435.593 | 0.565869
437.867 | 0.606814
440.137 | 0.648959
442.405 | 0.691133
444.669 | 0.731603
446.929 | 0.768233
449.187 | 0.799734
451.441 | 0.824182
453.691 | 0.839071
455.938 | 0.842363
458.182 | 0.833206
460.422 | 0.814464
462.659 | 0.788699
464.892 | 0.759086
467.121 | 0.730372
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

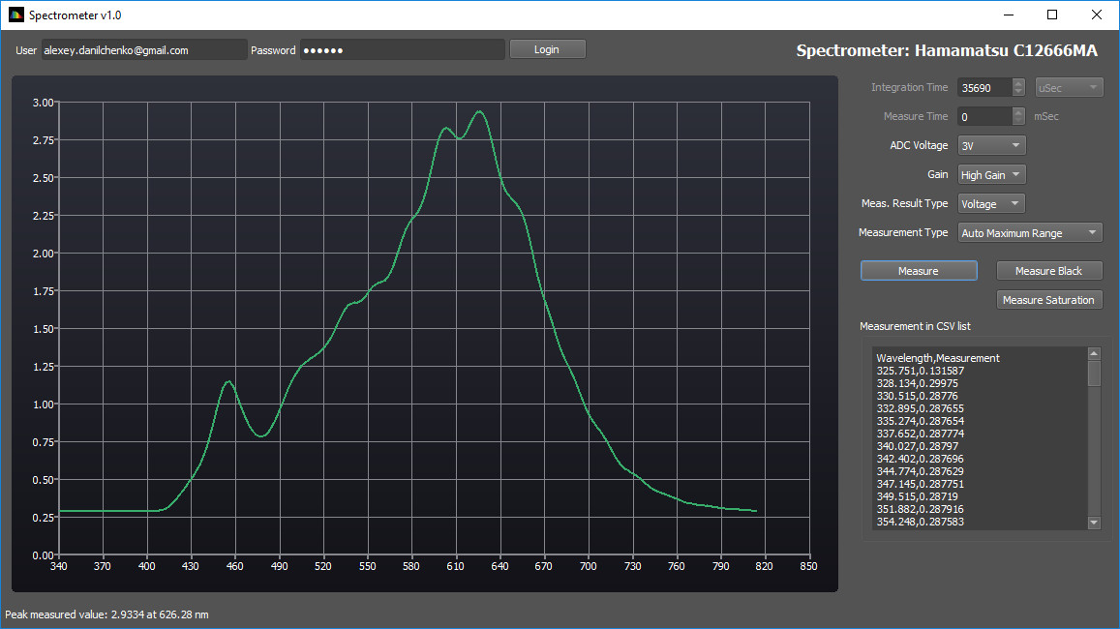
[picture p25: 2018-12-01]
software/common/images/Spectrometer.jpg

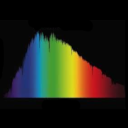
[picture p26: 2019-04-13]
software/common/images/SpectrometerApp.png

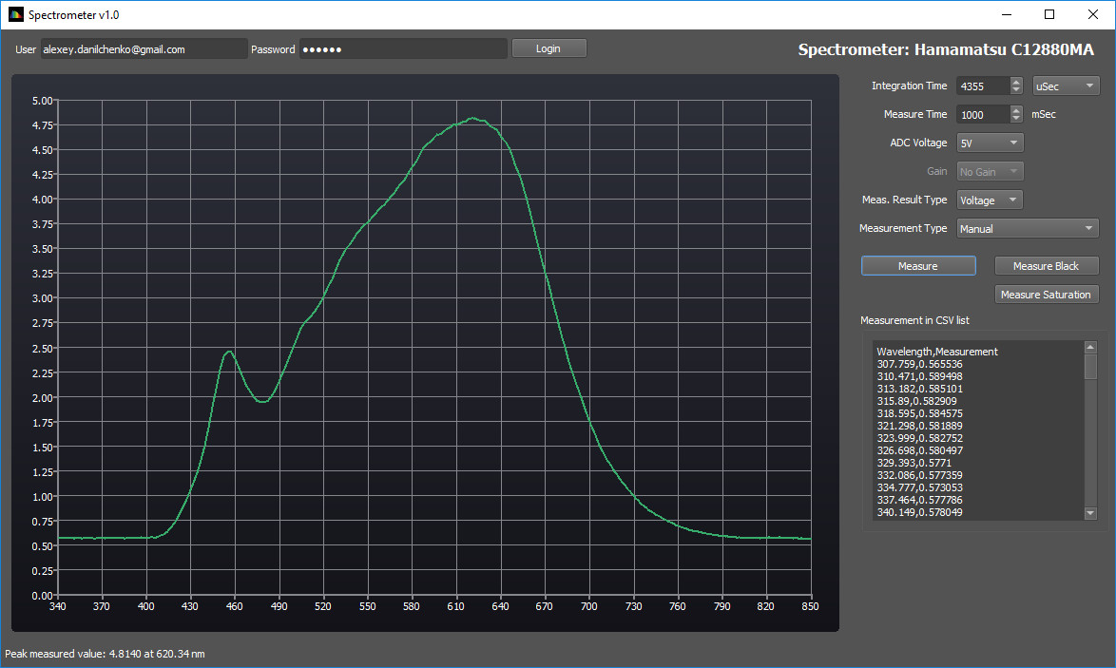
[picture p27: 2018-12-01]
software/common/images/Spectrometer2.jpg

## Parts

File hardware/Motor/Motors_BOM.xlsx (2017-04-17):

Qty | Value | Device | Package | Parts | Description | MPN | SUPPLIER | Distributor | Distributor Part Number
2 | 0.01 uF | C-EUC0805 | C0805 | C5, C6 | Multilayer Ceramic Capacitors MLCC - SMD/SMT 0805 0.01uF 100volts X7R 10% | C2012X7R2A103K085AA | TDK | Mouser | 810-C2012X7R2A103K
1 | 0.022 uF | C-EUC0805 | C0805 | C1 | Multilayer Ceramic Capacitors MLCC - SMD/SMT 0805 100volt 0.022uF X7R 10% Soft Term | GCJ216R72A223KA01D | Murata | Mouser | 81-GCJ216R72A223KA1D
1 | 0.1uF | C-EUC0805 | C0805 | c10, C11 | Multilayer Ceramic Capacitors MLCC - SMD/SMT 0805 0.1uF 25volts X7R 10% | GRM21BR71E104KA01L | Murata | Mouser | 81-GRM40X104K25L
1 | 0.22 uF | C-EUC0805 | C0805 | C2 | Multilayer Ceramic Capacitors MLCC - SMD/SMT 0805 0.22uF 25volts X7R 10% | GRM219R71E224KA01D | Murata | Mouser | 81-GRM21R71E224KA01D
2 | 0.47 uF | C-EUC0805 | C0805 | C3, C4 | Multilayer Ceramic Capacitors MLCC - SMD/SMT 0805 0.47uF 25volts X7R 10% | C2012X7R1E474K125AA | TDK | Mouser | 810-C2012X7R1E474K
1 | 100 K | R-EU_R0805 | R0805 | R2 | Thick Film Resistors - SMD 1/8watt 100Kohms 1% 100ppm | CRCW0805100KFKEA | Vishay | Mouser | 71-CRCW0805-100K-E3
1 | 100uF | CPOL-USCT7343 | CT7343 | C7 | Tantalum Capacitors - Polymer SMD 25volts 100uF 20% ESR=60mohms | T521X107M025ATE060 | Kemet | Mouser | 80-T521X107M25ATE60
4 | 10K | R-EU_R0805 | R0805 | R3, R4, R5, R6 | Thick Film Resistors - SMD 1/8watt 10Kohms 1% 100ppm | CRCW080510K0FKEA | Vishay | Mouser | 71-CRCW0805-10K-E3
1 | 47uF | CPOL-USCT7343 | CT7343 | C8, C9 | Tantalum Capacitors - Polymer SMD 35volts 47uF 20% ESR=30mohms | T521X476M035ATE030 | Kemet | Mouser | 80-T521X476M35ATE30
1 | 5K | R-EU_R0805 | R0805 | R1 | Thick Film Resistors - SMD 1/8watt 5Kohms 1% | CRCW08055K00FKTA | Vishay | Mouser | 71-CRCW0805-5K
2 | BSS138 | MOSFET-NCHANNELSMD | SOT23-3 | Q1, Q2 | MOSFET SOT-23 N-CH LOGIC | BSS138 | Fairchild Semiconductor | Mouser | 512-BSS138
1 | DRV8884PWPR | DRV8884PWPR |  | U1 | Motor/Motion/Ignition Controllers & Drivers 1.0A Stepper Motor Driver With 1/16 Microstepping and Integrated Current Sensing (STEP/DIR Ctrl) 24-HTSSOP -40 to 125 | DRV8884PWPR | Texas Instruments | Mouser | 595-DRV8884PWPR
1 | LS7083N-S | LS7083N-S |  | U3 | CMOS quadrature clock converter | LS7083N-S | LSI/CSI | OmniPro | LS7083N-S
1 | MC33269ST | MC33269ST | SOT223 | IC1 | LDO Voltage Regulators 3.3V ADJ 800mA | MC33269ST-3.3T3G | ON Semiconductor | Mouser | 863-MC33269ST-3.3T3G
1 | PMEG2010ER | DIODE-SOD123 | SOD123 | D1 | Schottky Diodes & Rectifiers SCHOTTKY LOW VF | PMEG2010ER,115 | NXP | Mouser | 771-PMEG2010ER115
1 | POWERSUPPLY_DC21MMX | POWERSUPPLY_DC21MMX | POWERSUPPLY_DC-21MM | DC1 | DC Power Connectors Power Jacks | PJ-102AH | CUI Inc. | Mouser | 490-PJ-102AH
1 | PHOTON | PHOTON Without Headers | PHOTON | U2 | WiFi/802.11 Development Tools Photon no headers | PHNTRAYNOH | Particle
2 | Photon socket | Preci-Dip 714-87-112-31-012101 |  |  |  | 714-87-112-31-012101 | Preci-Dip | DIGIKEY | 1212-1166-ND
2 | Photon headers for the sockets above | Preci-Dip 350-80-112-00-006101 |  |  |  | 350-80-112-00-006101, 350-PP-1NN-00-006101 series | Preci-Dip | RS-Online | 702-0095
1 | Rotary Connector | M04PTH | 1X04 | JP3 | Header 4
1 | Stepper Connector | M04PTH | 1X04 | JP1 | Header 4
1 | X1/X4 Jumper | M03PTH | 1X03 | JP2 | Header 3

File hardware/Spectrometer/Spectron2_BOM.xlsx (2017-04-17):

Qty | Value | Device | Package | Parts | Description | MPN | SUPPLIER | Distributor | Distributor Part Number
4 | 1uF | TANT-CAP1206 | EIA3216 | C1, C10, C21, C30 | Tantalum Capacitors - Solid SMD 1uF 25volts 10% A case Molded | 593D105X9025A2TE3 | Vishay | Mouser | 74-593D105X9025A2TE3
1 | 22uF | C-EUC0805 | C0805 | C11 | Multilayer Ceramic Capacitors MLCC - SMD/SMT 0805 22uF 25volts X5R 20% | GRM21BR61E226ME44L | Murata | Mouser | 81-GRM21BR61E226ME4L
6 | 10uF | C-EUC0805 | C0805 | C6, C7,C18, C19, C27, C29 | Multilayer Ceramic Capacitors MLCC - SMD/SMT 0805 10uF 35volts *Derate Voltage/Temp | GRM21BC71E106KE11L | Murata | Mouser | 81-GRM21BC8YA106KE1L
1 | 2.7 nF | C-EUC0805 | C0805 | C20 | Multilayer Ceramic Capacitors MLCC - SMD/SMT 0805 2700pF 25volt X7R +/-10% | GRM216R71E272KA01D | Murata | Mouser | 81-GRM216R71E272KA1D
17 | 0.1uF | C-EUC0805 | C0805 | C3, C4, C8, C12, C14, C15, C16, C17, C23, C24, C26, C28, C32, C33, C34 and C1, C1 for sensor boards | Multilayer Ceramic Capacitors MLCC - SMD/SMT 0805 0.1uF 25volts X7R 10% | GRM21BR71E104KA01L | Murata | Mouser | 81-GRM40X104K25L
2 | 47uF | CPOL-USCT7343 | CT7343 | C35, C36 | Tantalum Capacitors - Polymer SMD 35volts 47uF 20% ESR=30mohms | T521X476M035ATE030 | Kemet | Mouser | 80-T521X476M35ATE30
1 | 1uF | C-EUC0805 | C0805 | C5 | Multilayer Ceramic Capacitors MLCC - SMD/SMT | GRM21BR71H105KA12K | Murata | Mouser | 81-GRM21BR71H105KA2K
6 | 10uF | TANT-CAP1206 | EIA3216 | C2, C9, C13, C22, C25, C31 | Tantalum Capacitors - Solid SMD 10UF 25V 10% | F951E106KAAAQ2 | AVX | Mouser | 647-F951E106KAAAQ2
2 | PMEG2010ER | DIODE-SOD123 | SOD123 | D1, D2 | Schottky Diodes & Rectifiers SCHOTTKY LOW VF | PMEG2010ER,115 | NXP | Mouser | 771-PMEG2010ER115
3 | 10K | R-EU_R0805 | R0805 | R1, R2, R3 | Thick Film Resistors - SMD 1/8watt 10Kohms 1% 100ppm | CRCW080510K0FKEA | Vishay | Mouser | 71-CRCW0805-10K-E3
1 | 20K | R-EU_R0805 | R0805 | R4 | Thick Film Resistors - SMD 1/8watt 20Kohms 1% 100ppm | CRCW080520K0FKEA | Vishay | Mouser | 71-CRCW0805-20K-E3
1 | 20 R | R-EU_R0805 | R0805 | R5 | Thick Film Resistors - SMD 0805 20ohm 1% Anti Surge AEC-Q200 | ESR10EZPF20R0 | ROHM Semiconductor | Mouser | 755-ESR10EZPF20R0
1 | AD7980 | AD7980 |  | U8 | Analog to Digital Converters - ADC 16-Bit 1 MSPS | AD7980ARMZ | Analog Devices | Mouser | 584-AD7980ARMZR7
1 | AD8031 | AD8031 |  | U4 | Operational Amplifiers - Op Amps 2.7V 800uA 80Mhz RRIO SGL | AD8031ARTZ-REEL7 | Analog Devices | Mouser | 584-AD8031ARTZ-R7
1 | ADA4841 | ADA4841 |  | U6 | Operational Amplifiers - Op Amps Low Power Low Noise and Distort RRO | ADA4841-1YRJZ-R7 | Analog Devices | Mouser | 584-ADA4841-1YRJZ-R7
1 | ADG1604 | ADG1604 |  | U2 | Multiplexer Switch ICs 4:1 19MHz 950 mOhm CMOS | ADG1604BRUZ | Analog Devices | Mouser | 584-ADG1604BRUZ-R7
1 | ADG3304 | ADG3304 |  | U14 | Translation - Voltage Levels Low VTG 1.15V-5.5V 4-CH Bidirect Logic | ADG3304BRUZ-REEL7 | Analog Devices | Mouser | 584-ADG3304BRUZ-R7
1 | ADG821 | ADG821 |  | U13 | Analogue Switch ICs 500mOhm 5.5V CMOS Dual SPST | ADG821BRMZ-REEL7 | Analog Devices | Mouser | 584-ADG821BRMZ-R7
1 | ADP7142-2.5 | ADP7142 |  | U10 | LDO Voltage Regulators 40V 200mA LDO 2.5Vo | ADP7142AUJZ-2.5-R7 | Analog Devices | Mouser | 584-ADP7142AUJZ2.5R7
2 | ADP7142-5.0 | ADP7142 |  | U3, U7 | LDO Voltage Regulators 40V 200mA LDO 5.0Vo | ADP7142AUJZ-5.0-R7 | Analog Devices | Mouser | 584-ADP7142AUJZ5.0R7
1 | LM2662 | LM2662 |  | U15 | Voltage Regulators - Switching Regulators Switched Capacitor Vtg Cnvtr | LM2662MX/NOPB | Texas Instruments | Mouser | 926-LM2662MX/NOPB
1 | REF192 | REF192 |  | U1 | Voltage References 2.5V Prec Micropwr LDO Low VRef | REF192GSZ | Analog Devices | Mouser | 584-REF192GSZ-R7
1 | REF193 | REF193 |  | U5 | Voltage References 3V Prec Micropwr LDO | REF193GSZ | Analog Devices | Mouser | 584-REF193GSZ
1 | REF195 | REF195 |  | U11 | Voltage References 5V Prec Micropwr LDO Low VRef | REF195GSZ | Analog Devices | Mouser | 584-REF195GSZ-R
1 | REF198 | REF198 |  | U9 | Voltage References 4.096V Prec Micropwr LDO Low VRef | REF198GSZ | Analog Devices | Mouser | 584-REF198GSZ-R
1 | TLV809 | TLV809 |  | U12 | Supervisory Circuits 3Pin Supply Vltg Sup | TLV809K33DBVR | Texas Instruments | Mouser | 595-TLV809K33DBVR
1 | C12666/C12880 | Preci-Dip 350-80-108-00-006101 |  | JP1 | Header 8 | 714-87-112-31-012101 | Preci-Dip | RS-Online | 702-0060
1 | Trigger Pins | M05PTH | 1X05 | JP3 | Header 5
1 | POWERSUPPLY DC21MMX | POWERSUPPLY DC21MMX | POWERSUPPLY_DC-21MM | DC1 | DC Power Connectors Power Jacks | PJ-102AH | CUI Inc. | Mouser | 490-PJ-102AH
1 | PHOTON without headers | PHOTON without headers | PHOTON | U16 |  |  |  | Mouser
4 | Photon socket, sensor board socket | Preci-Dip 714-87-112-31-012101 |  |  |  | 714-87-112-31-012101 | Preci-Dip | DIGIKEY | 1212-1166-ND
2 | Photon headers for the sockets above | Preci-Dip 350-80-112-00-006101 |  |  |  | 350-80-112-00-006101, 350-PP-1NN-00-006101 series | Preci-Dip | RS-Online | 702-0095
1 | Spectrometer stand | MICRO SPECTROMETER |  |  | Hamamatsu Micro-Spectrometer C12666MA or C12880MA, part ordered is Preci-Dip stand | 115-87-314-41-003101 | Preci-Dip | DIGIKEY | 1212-1045-ND

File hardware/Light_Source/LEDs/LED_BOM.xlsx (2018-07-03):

Qty | Value | Device | Package | Parts | Description | MPN | SUPPLIER | Distributor | Distributor Part Number
2 | 39uF | CPOL-EUE | PANASONIC_E | C1,C15 | Aluminium Polymer Capacitor 39μF 50V dc 8mm E12 OS-CON Series, Surface Mount Polymer, ±20 | 50SVPF39M | Panasonic | RS-Online | 795-5427
2 | 10uF | C-EUC1206 | C1206 | C2,C16 | Multilayer Ceramic Capacitors MLCC - SMD/SMT SOFT 1206 35V 10uF X7R 20% | C3216X7R1V106M160AE | TDK | Mouser | 810-C3216X7R1V106M1E
4 | 1uF | C-EUC0805 | C0805 | C3,C9,C17,C20 | Multilayer Ceramic Capacitors MLCC - SMD/SMT SOFT 0805 50V 1uF X7R 20% | CGA4J3X7R1H105M125AE | TDK | Mouser | 810-CGA4J3X7R1H105MS
4 | 2.2uF | C-EUC1206 | C1206 | C4,C5,C18,C19 | Multilayer Ceramic Capacitors MLCC - SMD/SMT 1210 2.2uF 100volts X7R 20% | GCJ32DR72A225MA01L | Murata | Mouser | 81-GCJ32DR72A225M1L
2 | 10uF | CPOL-EUCT7343 | CT7343 | C6,C7 | Tantalum Capacitors - Polymer SMD 35V 10uF 2917 20% ESR=120mOhm AEC-Q200 | T591D106M035ATE120 | Kemet | Mouser | 80-T591D106M35ATE120
4 | 0.1uF | C-EUC0805 | C0805 | C8,C12,C13,C22 | Multilayer Ceramic Capacitors MLCC - SMD/SMT CEU 0805 50V 0.1uF X7R 10% | CEU4J2X7R1H104K125AE | TDK | Mouser | 810-CEU4J2X7R1H104K
1 | 10uF | TANT-CAP1206 | EIA3216 | C10 | Tantalum Capacitors - Solid SMD 25V 10uF 20% 1206 ESR= 2 Ohms | F951E106MAAAQ2 | AVX | Mouser | 647-F951E106MAAAQ2
2 | 2.2uF | C-EUC0805 | C0805 | C11,C21 | Multilayer Ceramic Capacitors MLCC - SMD/SMT SOFT 0805 50V 2.2uF X7R 20% | C2012X7R1H225M125AE | TDK | Mouser | 810-C2012X7R1H225M1E
2 | 1nF | C-EUC0805 | C0805 | C14,C23 | Multilayer Ceramic Capacitors MLCC - SMD/SMT WCAP-CSGP 1000pF 0805 10% 50V MLCC | 885012207086 | Wurth Electronics | Mouser | 710-885012207086
2 | 15m | R-EU_R1206 | R1206 | R1,R10 | Current Sense Resistors - SMD 0.5W 0.015 Ohm 1% | LVM12FTR015E-TR | Ohmite | Mouser | 588-LVM12FTR015E-TR
2 | 0.549 | R-EU_R1206 | R1206 | R2,R11 | 588-LVM12FTR015E-TR | SR732BTTER549F | KOA Speer | Mouser | 660-SR732BTTER549F
2 | 1M | R-EU_R0805 | R0805 | R3,R12 | Thick Film Resistors - SMD 0805 1Mohms 1% Anti-Surge AEC-Q200 | ERJ-P6WF1004V | Panasonic | Mouser | 667-ERJ-P6WF1004V
2 | 22.6K | R-EU_R0805 | R0805 | R4,R13 | Thick Film Resistors - SMD 1/8watt 22.6Kohms 1% 100ppm | CRCW080522K6FKEA | Vishay | Mouser | 71-CRCW0805-22.6K-E3
2 | 10K | R-EU_R0805 | R0805 | R8,R16 | Thick Film Resistors - SMD 10kohms .25W 1% TCR100 RES SMD | CRS0805-FX-1002ELF | Bourns | Mouser | 652-CRS0805FX1002ELF
2 | 90.9K | R-EU_R0805 | R0805 | R9,R17 | Thick Film Resistors - SMD 0805 90.9Kohms 1% AEC-Q200 | ERJ-6ENF9092V | Panasonic | Mouser | 667-ERJ-6ENF9092V
5 | 100K | R-EU_R0805 | R0805 | R5,R6,R7,R14,R15 | Thick Film Resistors - SMD Thick Film Resistors - SMD 0805 100Kohms 5% AEC-Q200 | ERJ-6GEYJ104V | Panasonic | Mouser | 667-ERJ-6GEYJ104V
2 | VSSAF3M10 | VSSAF3M10-M3_H | SODFL5226X100N | D1,D3 | Schottky Diodes & Rectifiers TMBS 100V Vrrm eSMP SlimSMA (DO-221AC) | VSSAF3M10-M3/H | Vishay | Mouser | 78-VSSAF3M10-M3/H
2 | ES1B-13-F | DIODESMA-ALT | SMA-DIODE_ALT | D2,D4 | Rectifiers 100V 1A | ES1B-13-F | Diodes Incorporated | Mouser | 621-ES1B-F
2 | Si2309CDS | MOSFET-PCHANNEL | SOT23-3 | Q1,Q2 | MOSFET -60V Vds 20V Vgs SOT-23 | SI2309CDS-T1-GE3 | Vishay | Mouser | 781-SI2309CDS-GE3
2 | 10uH | XAL1010-103 | XAL1010 | L1,L2 | Fixed Inductors 10uH 20% 15.5A 14.75mOhms AEC-Q200 | XAL1010-103MED | Coilcraft | Mouser | 994-XAL1010-103MED
1 | LT1129 | LT1129CST5 | SOT223 | IC1 | LDO Voltage Regulators 700mA Micropower Low Dropout Regulator with Shutdown | LT1129CST-5#PBF | Linear Technology | Mouser | 584-LT1129CST-5#PBF
1 | LT3952 | LT3952EFEPBFTSSOP-28_FE/EB-M | TSSOP-28_FE/EB-M | U1,U4 | LED Lighting Drivers 60V LED Driver with 4A Switch Current | LT3952HFE#PBF | Linear Technology | Linear Technology | LT3952HFE#PBF
1 | ADG1401 | ADG1401BRMZ | SOP65P490X110-8N | U2 | Analogue Switch ICs IC 1 Ohm 16.5V iCMOS SPST | ADG1401BRMZ | Analog Devices | Mouser | 584-ADG1401BRMZ
1 | PHOTON without headers | PHOTON without headers | PHOTON | U3
2 | Photon socket | Preci-Dip 714-87-112-31-012101 |  |  |  | 714-87-112-31-012101 | Preci-Dip | DIGIKEY | 1212-1166-ND
2 | Photon headers for the sockets above | Preci-Dip 350-80-112-00-006101 |  |  |  | 350-80-112-00-006101, 350-PP-1NN-00-006101 series | Preci-Dip | RS-Online | 702-0095
3 | +12V,LED Outputs | Terminal Block |  | J1,J2,J3 | 5mm Pitch Straight, PCB Terminal Block, PCB Mount, 2 Way | 282836-2 | TE Connectivity | RS-Online | 361-7667

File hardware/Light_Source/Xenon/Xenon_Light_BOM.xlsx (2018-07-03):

Qty | Value | Device | Package | Parts | Description | MPN | SUPPLIER | Distributor | Distributor Part Number
3 | 1uF | TANT-CAP1206 | EIA3216 | C2, C7, C10 | Tantalum Capacitors - Solid SMD 1uF 35V 20% A case | TMCMA1V105MTRF | Vishay | Mouser | 74-TMCMA1V105MTRF
7 | 0.1uF | C-EUC0805 | C0805 | C1,C3,C4,C6,C8,C11,C12 | Multilayer Ceramic Capacitors MLCC - SMD/SMT CEU 0805 50V 0.1uF X7R 10% | CEU4J2X7R1H104K125AE | TDK | Mouser | 810-CEU4J2X7R1H104K
2 | 10uF | TANT-CAP1206 | EIA3216 | C5,C9 | Tantalum Capacitors - Solid SMD 25V 10uF 20% 1206 ESR= 2 Ohms | F951E106MAAAQ2 | AVX | Mouser | 647-F951E106MAAAQ2
2 | 100K | R-EU_R0805 | R0805 | R1, R2 | Thick Film Resistors - SMD Thick Film Resistors - SMD 0805 100Kohms 5% AEC-Q200 | ERJ-6GEYJ104V | Panasonic | Mouser | 667-ERJ-6GEYJ104V
1 | LM3480-15 | LM3480 | SOT23 | U1 | LDO Voltage Regulators 100mA Quasi LDO Linear Vtg Reg | LM3480IM3X-15/NOPB | Texas Instruments | Mouser | 926-LM3480IM3X15NOPB
1 | R-78E5.0-1.0 | R-78E5.0-1.0 | R-78E5.0-1.0 | U2 | Non-Isolated DC/DC Converters 8-28Vin 5V 1.0A THRU | R-78E5.0-1.0 | RECOM Power | Mouser | 919-R-78E5.0-1.0
1 | MAX5312 | MAX5312 | SSOP16 | U3 | Digital to Analog Converters - DAC 12-Bit Precision DAC | MAX5312EAE+ | Maxim Integrated | Mouser | 700-MAX5312EAE
1 | ADG1401 | ADG1401BRMZ | SOP65P490X110-8N | U5 | Analogue Switch ICs IC 1 Ohm 16.5V iCMOS SPST | ADG1401BRMZ | Analog Devices | Mouser | 584-ADG1401BRMZ
1 | REF195 | REF195 | SOIC127P600X175-8N | U6 | Voltage References 5V Prec Micropwr LDO Low VRef | REF195GSZ | Analog Devices | Mouser | 584-REF195GSZ-R
1 | PHOTON without headers | PHOTON without headers | PHOTON | U4 |  |  |  | Mouser
2 | Photon socket | Preci-Dip 714-87-112-31-012101 |  |  |  | 714-87-112-31-012101 | Preci-Dip | DIGIKEY | 1212-1166-ND
2 | Photon headers for the sockets above | Preci-Dip 350-80-112-00-006101 |  |  |  | 350-80-112-00-006101, 350-PP-1NN-00-006101 series | Preci-Dip | RS-Online | 702-0095
1 | Xenon PSU | Terminal Block |  | J2 | 5mm Pitch Straight, PCB Terminal Block, PCB Mount, 4 Way | 897-0856 | RS Pro | RS-Online | 897-0856
1 | +24V | Terminal Block |  | J1 | 5mm Pitch Straight, PCB Terminal Block, PCB Mount, 2 Way | 282836-2 | TE Connectivity | RS-Online | 361-7667

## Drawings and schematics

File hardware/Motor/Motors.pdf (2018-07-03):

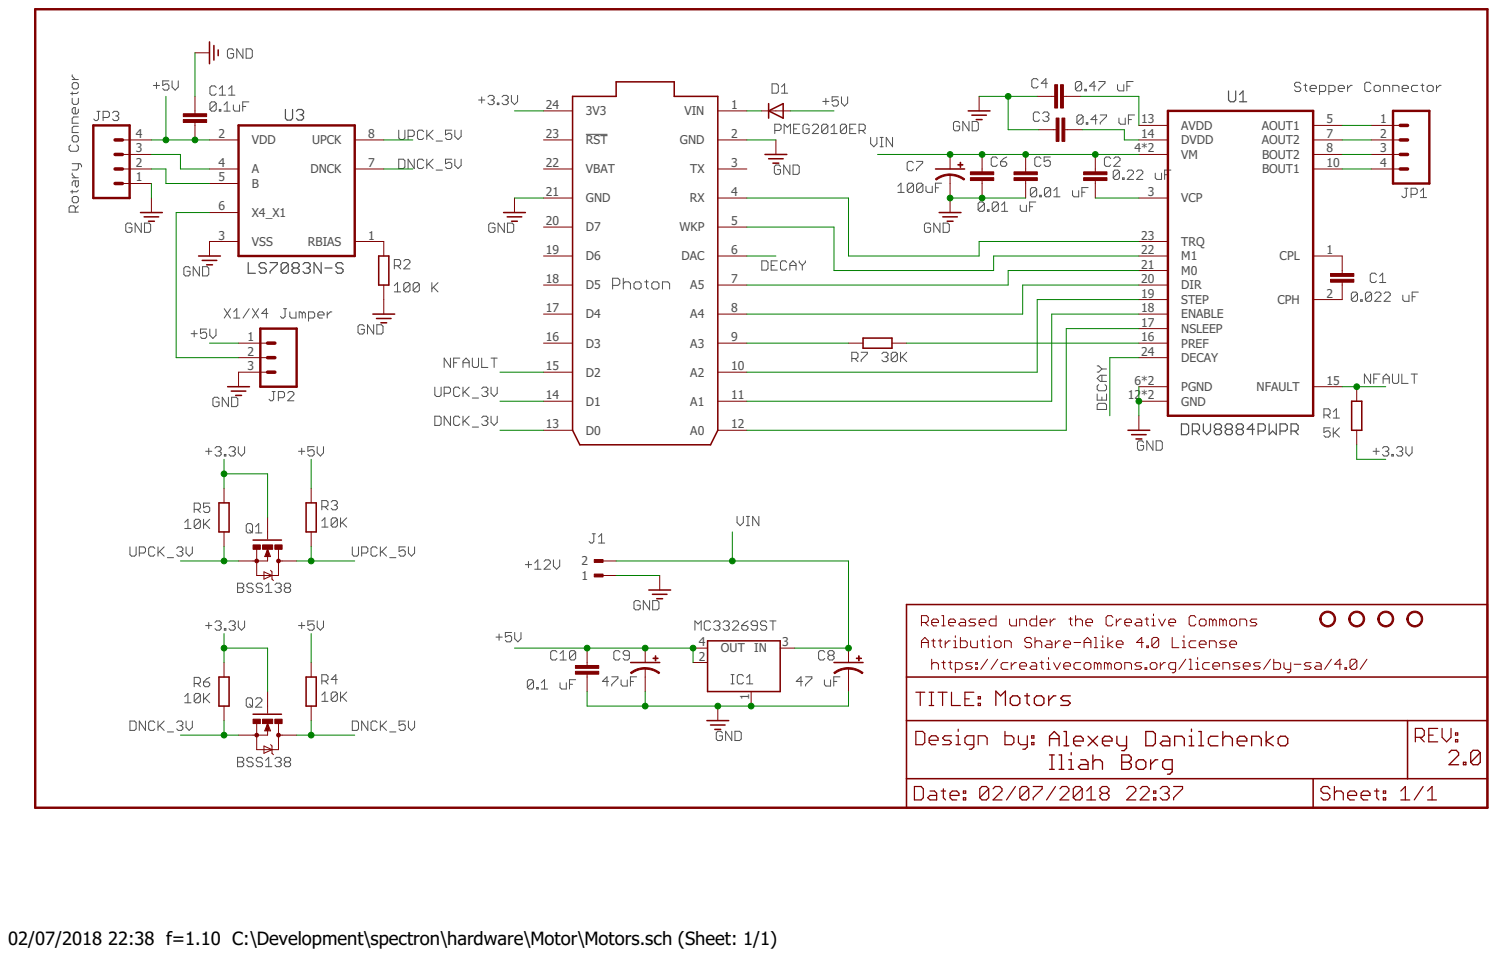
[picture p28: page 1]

02/07/2018 22:38 f=1.10 C:\Development\spectron\hardware\Motor\Motors.sch (Sheet: 1/1)

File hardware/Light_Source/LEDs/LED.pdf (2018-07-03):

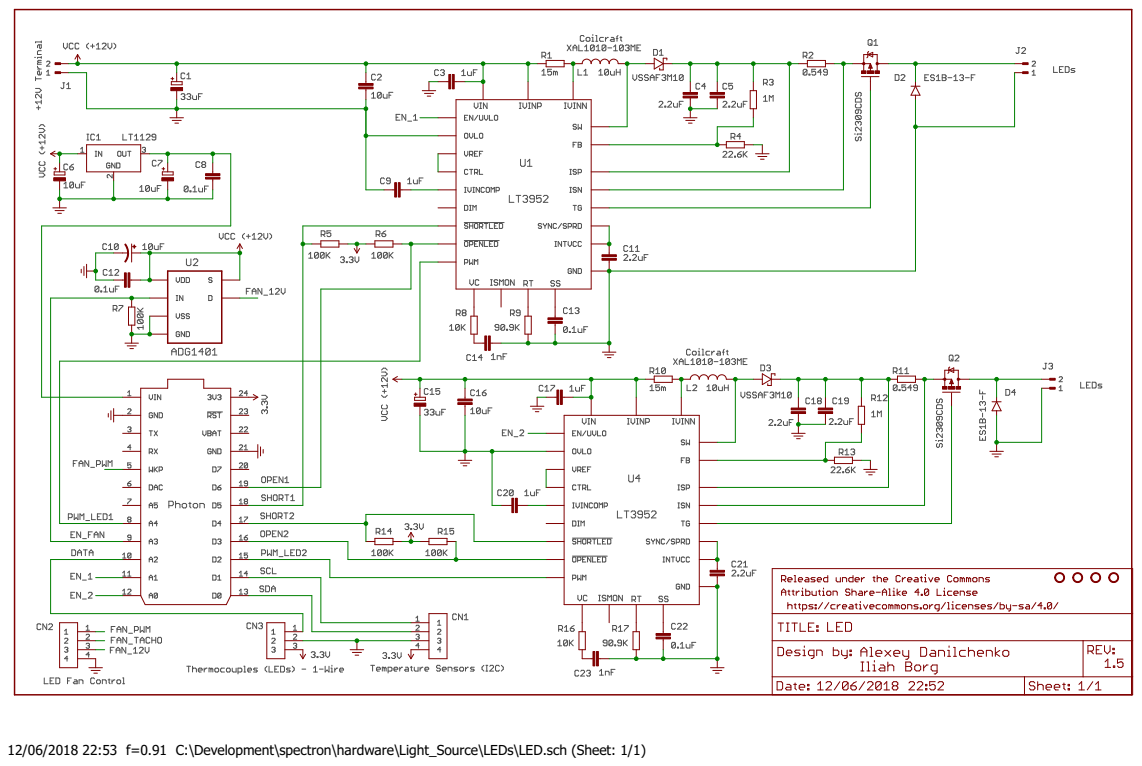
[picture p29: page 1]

12/06/2018 22:53 f=0.91 C:\Development\spectron\hardware\Light_Source\LEDs\LED.sch (Sheet: 1/1)

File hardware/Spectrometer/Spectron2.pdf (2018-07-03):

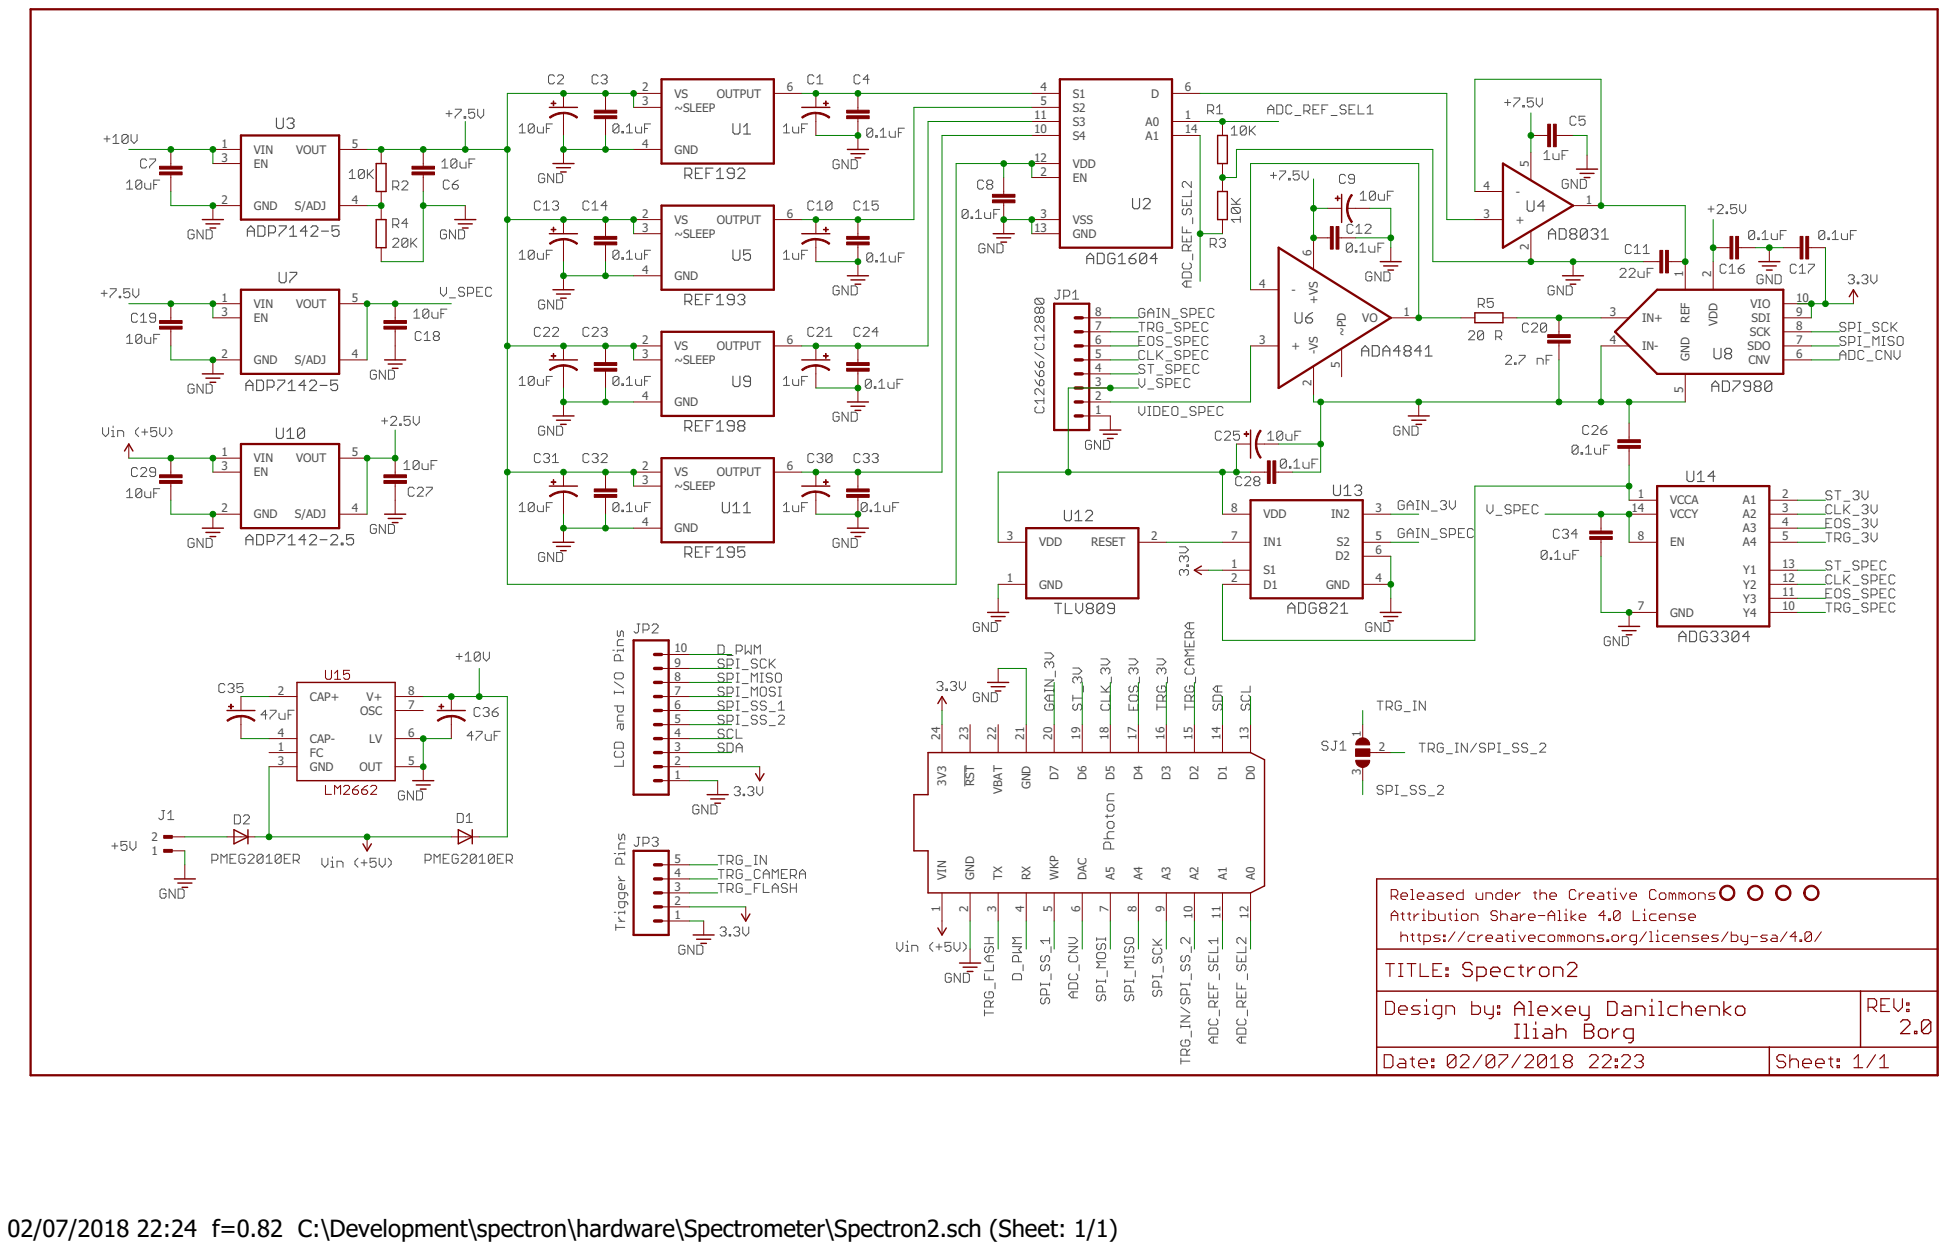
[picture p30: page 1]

02/07/2018 22:24 f=0.82 C:\Development\spectron\hardware\Spectrometer\Spectron2.sch (Sheet: 1/1)

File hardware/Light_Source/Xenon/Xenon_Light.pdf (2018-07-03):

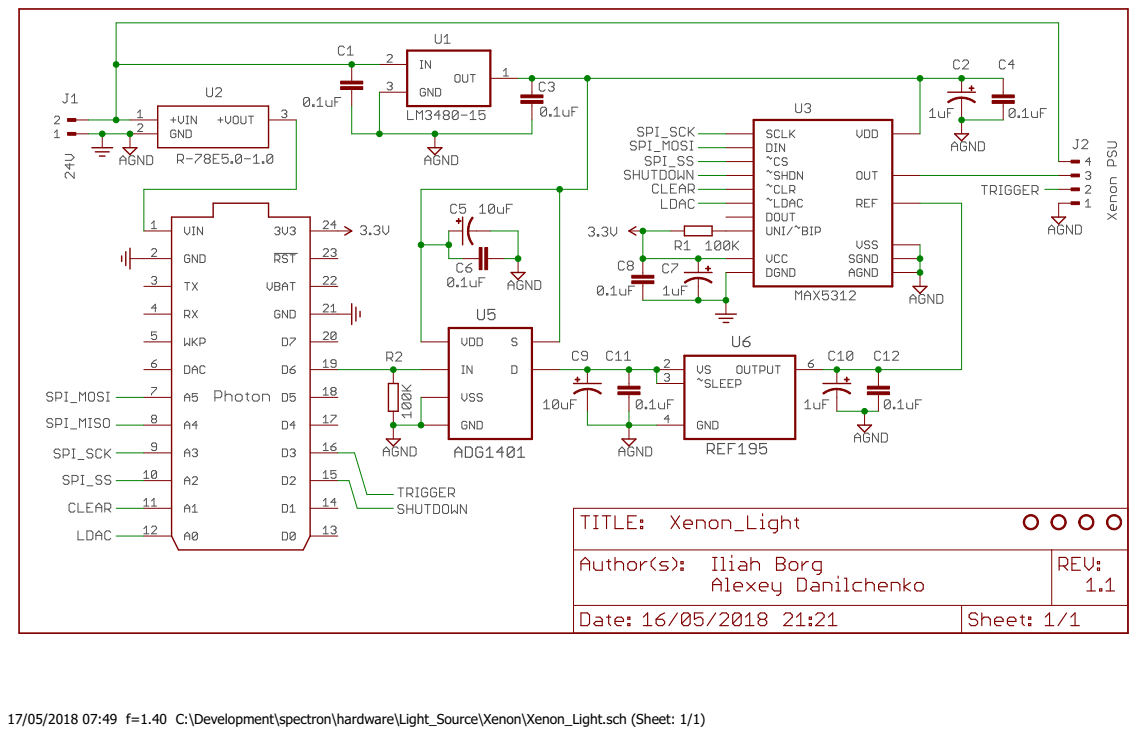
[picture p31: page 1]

17/05/2018 07:49 f=1.40 C:\Development\spectron\hardware\Light_Source\Xenon\Xenon_Light.sch (Sheet: 1/1)

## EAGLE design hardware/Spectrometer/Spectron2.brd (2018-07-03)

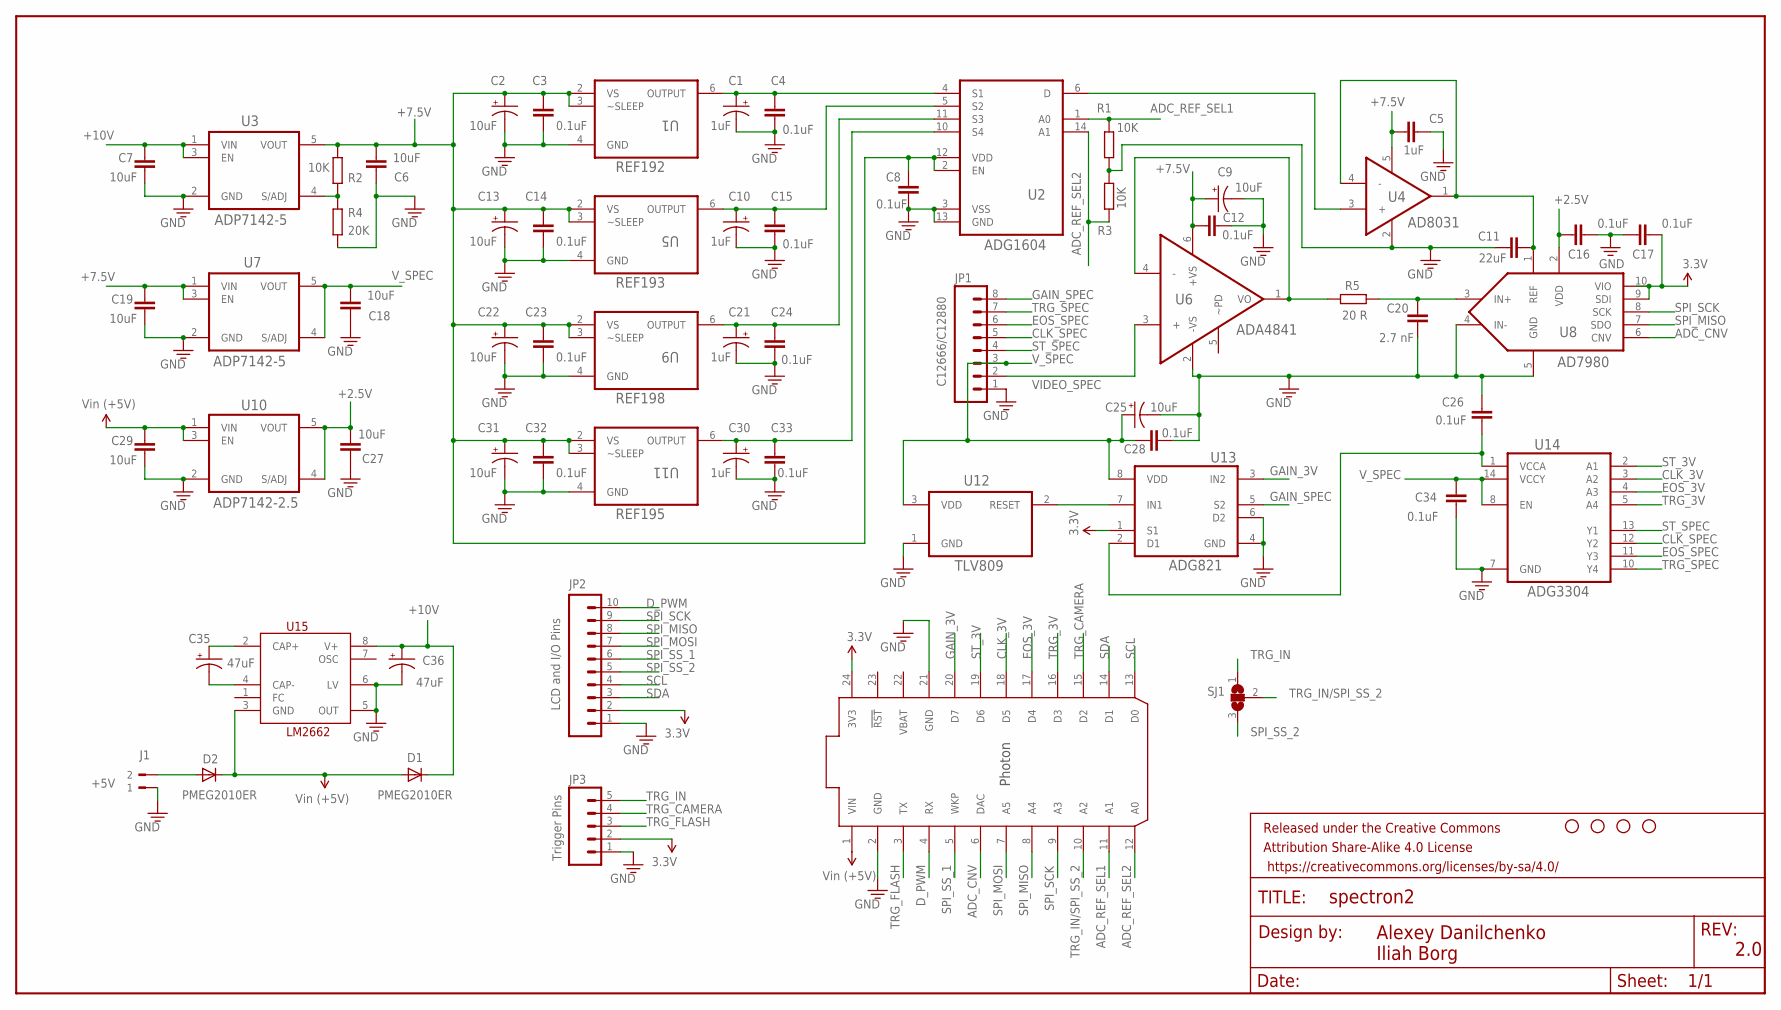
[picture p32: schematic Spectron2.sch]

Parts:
C1, C10, C21, C30: 1uF; EIA3216
C2, C9, C13, C22, C25, C31: 10uF; EIA3216
C3, C4, C8, C12, C14, C15, C16, C17, C23, C24, C26, C28, C32, C33, C34: 0.1uF; C0805
C5: 1uF; C0805
C6, C7, C18, C19, C27, C29: 10uF; C0805
C11: 22uF; 1206
C20: 2.7 nF; C0805
C35, C36: 47uF; CT7343
D1, D2: PMEG2010ER; SOD123
FRAME1: FRAME-LEDGER; CREATIVE_COMMONS
J1: +5V; WEIDMULLER_PM5.08_2
JP1: C12666/C12880; 1X08
JP2: LCD and I/O Pins; 1X10
JP3: Trigger Pins; 1X05
R1, R2, R3: 10K; R0805
R4: 20K; R0805
R5: 20 R; R0805
SJ1: SJ2W; SJ_2
STANDOFF1, STANDOFF2, STANDOFF3, STANDOFF4: STAND-OFF
U1: REF192; SOIC127P600X175-8N
U2: ADG1604; SOP65P640X120-14N
U3, U7: ADP7142-5; SOT95P280X145-5N
U4: AD8031; SOT95P280X145-5N
U5: REF193; SOIC127P600X175-8N
U6: ADA4841; SOT95P280X145-6N
U8: AD7980; SOP50P490X110-10N
U9: REF198; SOIC127P600X175-8N
U10: ADP7142-2.5; SOT95P280X145-5N
U11: REF195; SOIC127P600X175-8N
U12: TLV809; SOT95P237X112-3N
U13: ADG821; SOP65P490X110-8N
U14: ADG3304; SOP65P640X120-14N
U15: LM2662; SOIC8
U16: PHOTON_WITH_HEADERS; PHOTON

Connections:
3.3V: C17.2, JP2.2, JP3.2, U8.9 (SDI), U8.10 (VIO), U13.1 (S1), U16.24 (3V3)
+2.5V: C16.1, C27.1, U8.2 (VDD), U10.4 (S/ADJ), U10.5 (VOUT)
+7.5V: C2.A (+), C3.2, C5.2, C6.1, C8.2, C9.A (+), C12.2, C13.A (+), C14.2, C19.2, C22.A (+), C23.2, C31.A (+), C32.2, R2.1, U1.2 (VS), U1.3 (~SLEEP), U2.2 (EN), U2.12 (VDD), U3.5 (VOUT), U4.5 (+VS), U5.2 (VS), U5.3 (~SLEEP), U6.6 (+VS), U7.1 (VIN), U7.3 (EN), U9.2 (VS), U9.3 (~SLEEP), U11.2 (VS), U11.3 (~SLEEP)
+10V: C7.2, C36.+, D1.C, U3.1 (VIN), U3.3 (EN), U15.8 (V+)
ADC_CNV: U8.6 (CNV), U16.6 (DAC)
ADC_REF_SEL1: R1.1, U2.1 (A0), U16.11 (A1)
ADC_REF_SEL2: R3.2, U2.14 (A1), U16.12 (A0)
CLK_3V: U14.3 (A2), U16.18 (D5)
CLK_SPEC: JP1.5, U14.12 (Y2)
D_PWM: JP2.10, U16.4 (RX)
EOS_3V: U14.4 (A3), U16.17 (D4)
EOS_SPEC: JP1.6, U14.11 (Y3)
GAIN_3V: U13.3 (IN2), U16.20 (D7)
GAIN_SPEC: JP1.8, U13.5 (S2)
GND: C1.C (-), C2.C (-), C3.1, C4.1, C5.1, C6.2, C7.1, C8.1, C9.C (-), C10.C (-), C11.1, C12.1, C13.C (-), C14.1, C15.1, C16.2, C17.1, C18.2, C19.1, C20.1, C21.C (-), C22.C (-), C23.1, C24.1, C25.C (-), C26.2, C27.2, C28.1, C29.1, C30.C (-), C31.C (-), C32.1, C33.1, C34.1, C36.-, J1.1, JP1.1, JP2.1, JP3.1, R1.2, R3.1, R4.2, U1.4 (GND), U2.3 (VSS), U2.13 (GND), U3.2 (GND), U4.2 (-VS), U5.4 (GND), U6.2 (-VS), U7.2 (GND), U8.4 (IN-), U8.5 (GND), U9.4 (GND), U10.2 (GND), U11.4 (GND), U12.1 (GND), U13.4 (GND), U13.6 (D2), U14.7 (GND), U15.5 (OUT), U15.6 (LV), U16.2 (GND), U16.21 (GND)
unnamed: R2.2, R4.1, U3.4 (S/ADJ)
unnamed: C11.2, U4.1 (VOUT), U4.4 (-), U8.1 (REF)
unnamed: C21.A (+), C24.2, U2.11 (S3), U9.6 (OUTPUT)
unnamed: R5.2, U6.1 (VO), U6.4 (-)
unnamed: U12.2 (RESET), U13.7 (IN1)
unnamed: C1.A (+), C4.2, U1.6 (OUTPUT), U2.4 (S1)
unnamed: U2.6 (D), U4.3 (+)
unnamed: C10.A (+), C15.2, U2.5 (S2), U5.6 (OUTPUT)
unnamed: C30.A (+), C33.2, U2.10 (S4), U11.6 (OUTPUT)
unnamed: D2.A, J1.2
unnamed: C20.2, R5.1, U8.3 (IN+)
unnamed: C35.-, U15.4 (CAP-)
unnamed: C35.+, U15.2 (CAP+)
unnamed: C26.1, U13.2 (D1), U14.1 (VCCA)
SCL: JP2.4, U16.13 (D0)
SDA: JP2.3, U16.14 (D1)
SPI_MISO: JP2.8, U8.7 (SDO), U16.8 (A4)
SPI_MOSI: JP2.7, U16.7 (A5)
SPI_SCK: JP2.9, U8.8 (SCK), U16.9 (A3)
SPI_SS_1: JP2.6, U16.5 (WKP)
SPI_SS_2: JP2.5, SJ1.3
ST_3V: U14.2 (A1), U16.19 (D6)
ST_SPEC: JP1.4, U14.13 (Y1)
TRG_3V: U14.5 (A4), U16.16 (D3)
TRG_CAMERA: JP3.4, U16.15 (D2)
TRG_FLASH: JP3.3, U16.3 (TX)
TRG_IN: JP3.5, SJ1.1
TRG_IN/SPI_SS_2: SJ1.2, U16.10 (A2)
TRG_SPEC: JP1.7, U14.10 (Y4)
VBAT: U16.22 (VBAT)
VIDEO_SPEC: JP1.2, U6.3 (+)
VIN: C29.2, D1.A, D2.C, U10.1 (VIN), U10.3 (EN), U15.3 (GND), U16.1 (VIN)
V_SPEC: C18.1, C25.A (+), C28.2, C34.2, JP1.3, U7.4 (S/ADJ), U7.5 (VOUT), U12.3 (VDD), U13.8 (VDD), U14.8 (EN), U14.14 (VCCY)

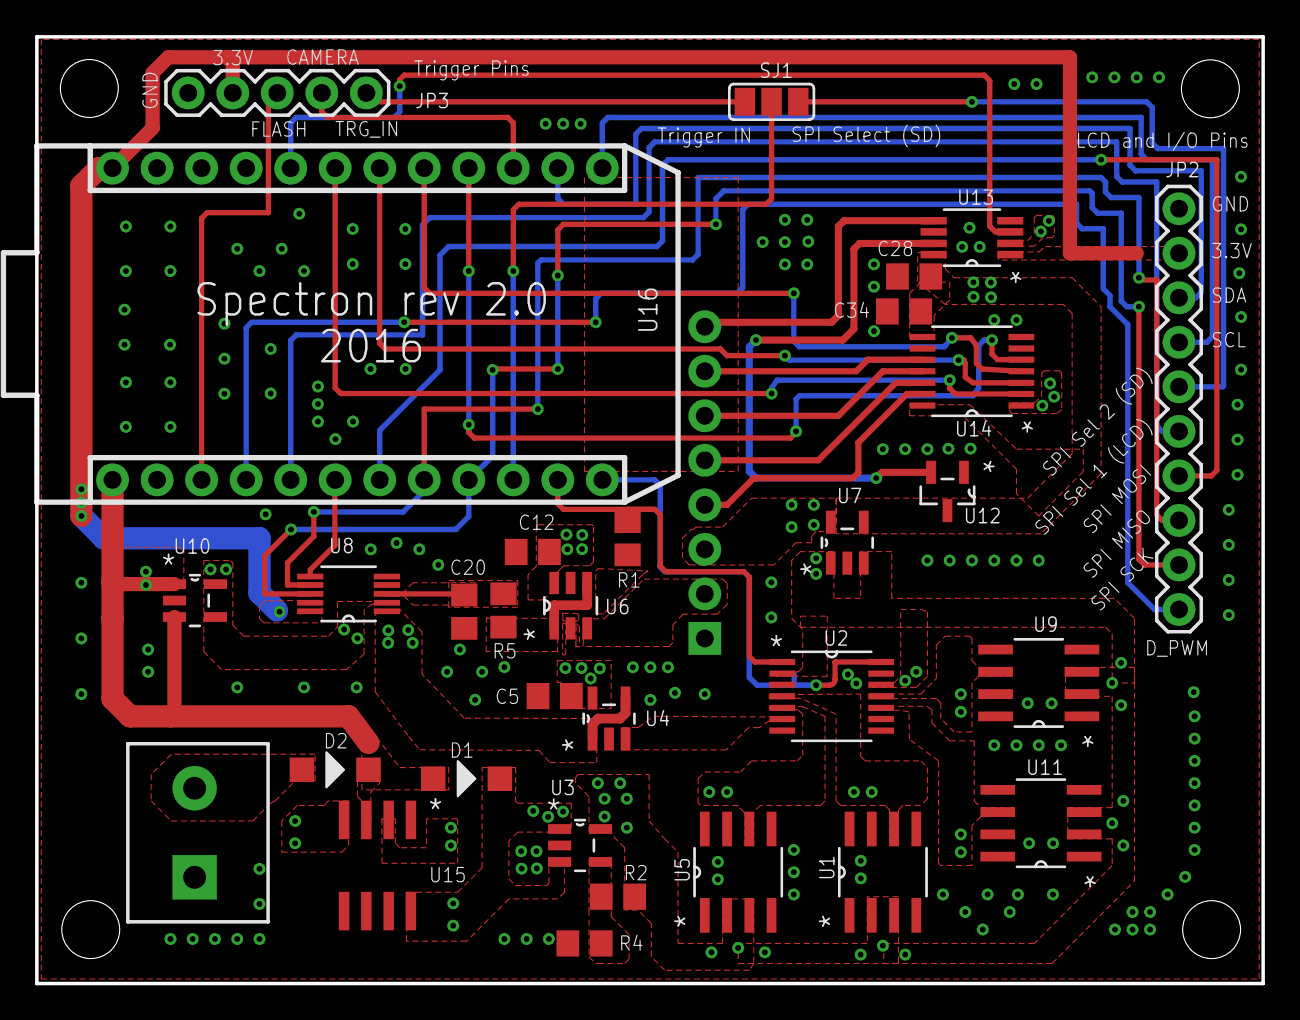
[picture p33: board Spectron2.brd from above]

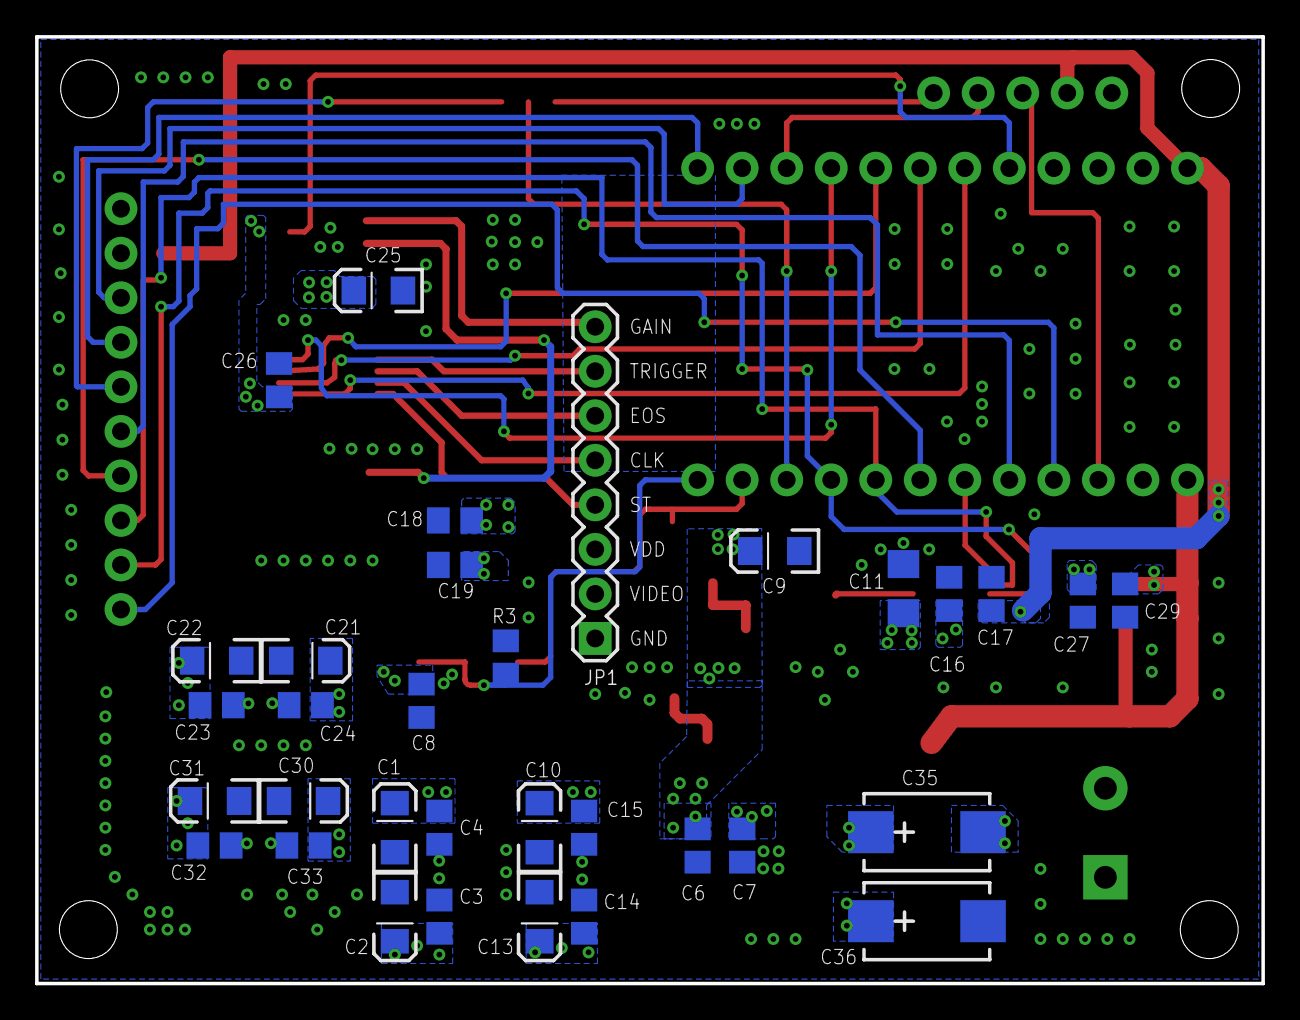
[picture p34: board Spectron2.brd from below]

Board: 2 copper layers, 70.0 x 54.0 mm, 69 parts (33 on the bottom side), 47 nets.

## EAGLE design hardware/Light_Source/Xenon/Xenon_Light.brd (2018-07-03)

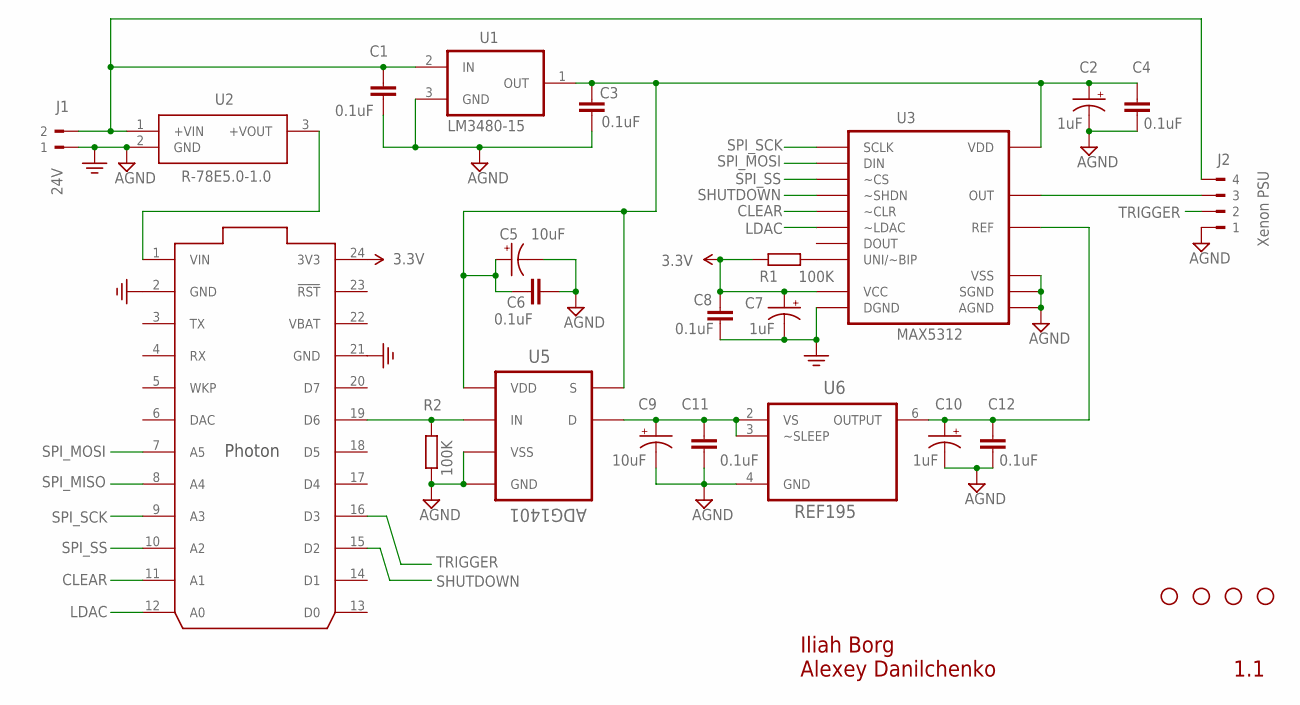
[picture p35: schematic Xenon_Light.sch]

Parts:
C1, C3, C4, C6, C8, C11, C12: 0.1uF; C0805
C2, C7, C10: 1uF; EIA3216
C5, C9: 10uF; EIA3216
J1: 24V; WEIDMULLER_PM5.08_2
J2: Xenon PSU; TERMINAL_BLK_4X5MM
R1, R2: 100K; R0805
STANDOFF1, STANDOFF2, STANDOFF3, STANDOFF4: STAND-OFF
U1: LM3480-15; SOT23
U2: R-78E5.0-1.0
U3: MAX5312; SSOP16
U4: PHOTON_WITH_HEADERS; PHOTON
U5: ADG1401; SOP65P490X110-8N
U6: REF195; SOIC127P600X175-8N

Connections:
3.3V: C7.A (+), C8.2, R1.2, U3.6 (VCC), U4.24 (3V3)
15V: C9.A (+), C11.2, U5.8 (D), U6.2 (VS), U6.3 (~SLEEP)
CLEAR: U3.15 (~CLR), U4.11 (A1)
GND: C1.1, C2.C (-), C3.1, C4.1, C5.C (-), C6.1, C7.C (-), C8.1, C9.C (-), C10.C (-), C11.1, C12.1, J1.1, J2.1, R2.1, U1.3 (GND), U2.2 (GND), U3.5 (DGND), U3.10 (SGND), U3.11 (AGND), U3.12 (VSS), U4.2 (GND), U4.21 (GND), U5.3 (GND), U5.7 (VSS), U6.4 (GND)
LDAC: U3.16 (~LDAC), U4.12 (A0)
unnamed: C1.2, J1.2, J2.4, U1.2 (IN), U2.1 (+VIN)
unnamed: U2.3 (+VOUT), U4.1 (VIN)
unnamed: R2.2, U4.19 (D6), U5.6 (IN)
unnamed: R1.1, U3.8 (UNI/~BIP)
unnamed: J2.3, U3.9 (OUT)
REF: C10.A (+), C12.2, U3.13 (REF), U6.6 (OUTPUT)
SHUTDOWN: U3.7 (~SHDN), U4.15 (D2)
SPI_MISO: U4.8 (A4)
SPI_MOSI: U3.2 (DIN), U4.7 (A5)
SPI_SCK: U3.1 (SCLK), U4.9 (A3)
SPI_SS: U3.3 (~CS), U4.10 (A2)
TRIGGER: J2.2, U4.16 (D3)
V15V: C2.A (+), C3.2, C4.2, C5.A (+), C6.2, U1.1 (OUT), U3.14 (VDD), U5.1 (S), U5.4 (VDD)
VBAT: U4.22 (VBAT)

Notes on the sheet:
1.1
Iliah Borg Alexey Danilchenko

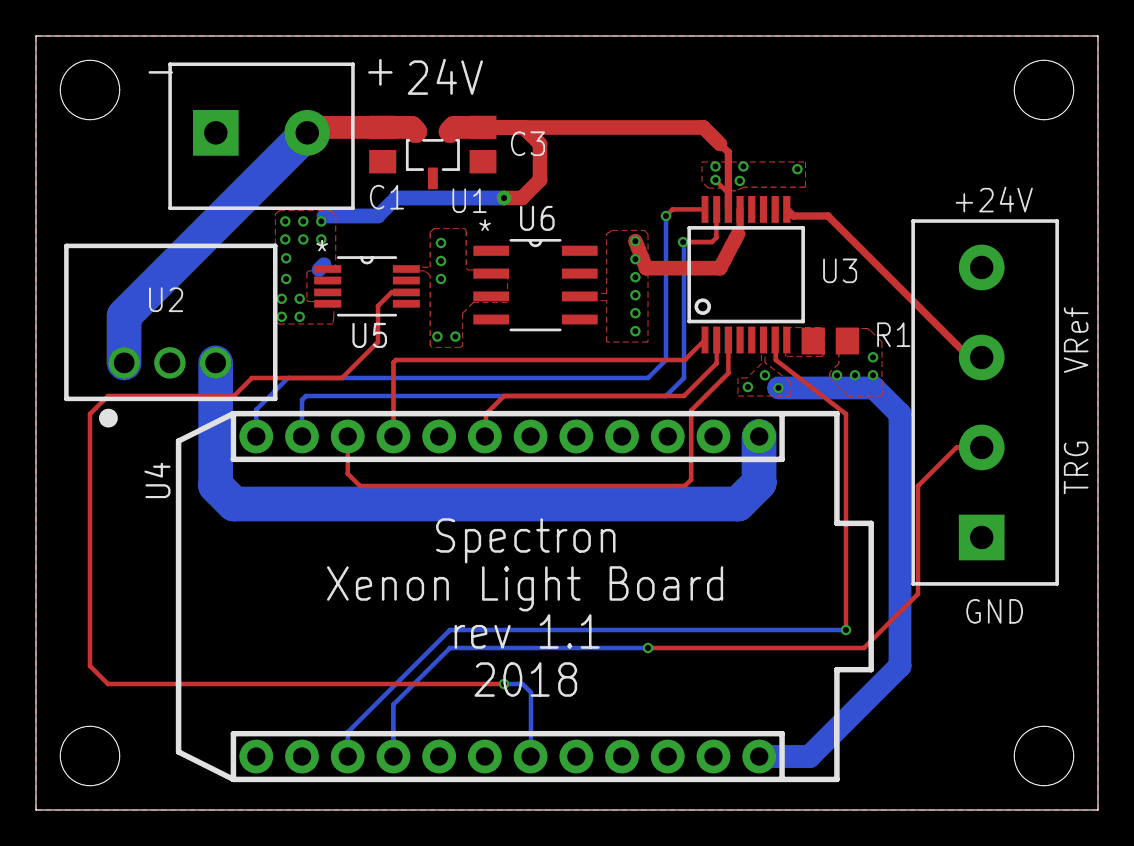
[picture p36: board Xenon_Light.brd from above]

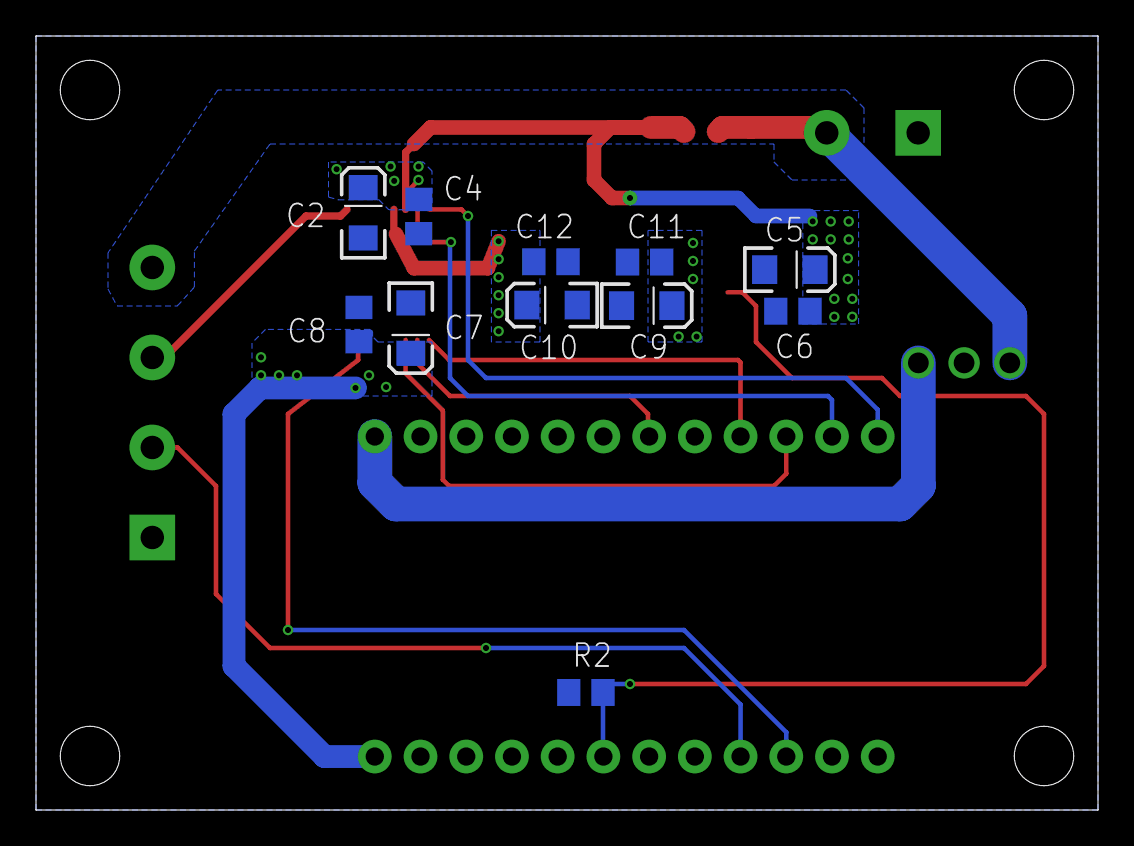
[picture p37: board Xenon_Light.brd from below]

Board: 2 copper layers, 59.0 x 43.0 mm, 26 parts (11 on the bottom side), 17 nets.

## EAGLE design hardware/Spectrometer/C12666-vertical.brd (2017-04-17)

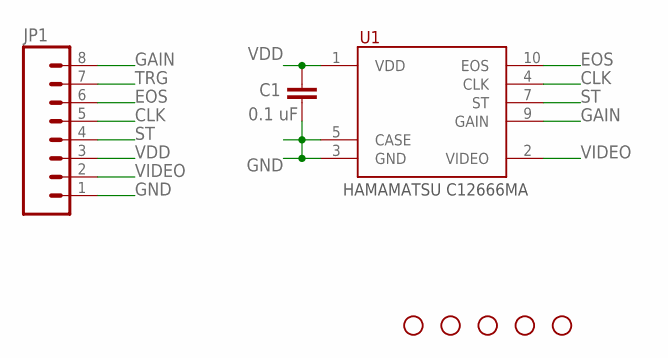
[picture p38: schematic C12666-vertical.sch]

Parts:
C1: 0.1 uF; C0805
JP1: M08SILK_FEMALE_PTH; 1X08
STANDOFF1, STANDOFF2, STANDOFF3, STANDOFF4, STANDOFF5: STAND-OFF
U1: MICROSPEC-C12666MA; C12666MA

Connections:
CLK: JP1.5, U1.4 (CLK)
EOS: JP1.6, U1.10 (EOS)
GAIN: JP1.8, U1.9 (GAIN)
GND: C1.2, JP1.1, U1.3 (GND), U1.5 (CASE)
ST: JP1.4, U1.7 (ST)
TRG: JP1.7
VDD: C1.1, JP1.3, U1.1 (VDD)
VIDEO: JP1.2, U1.2 (VIDEO)

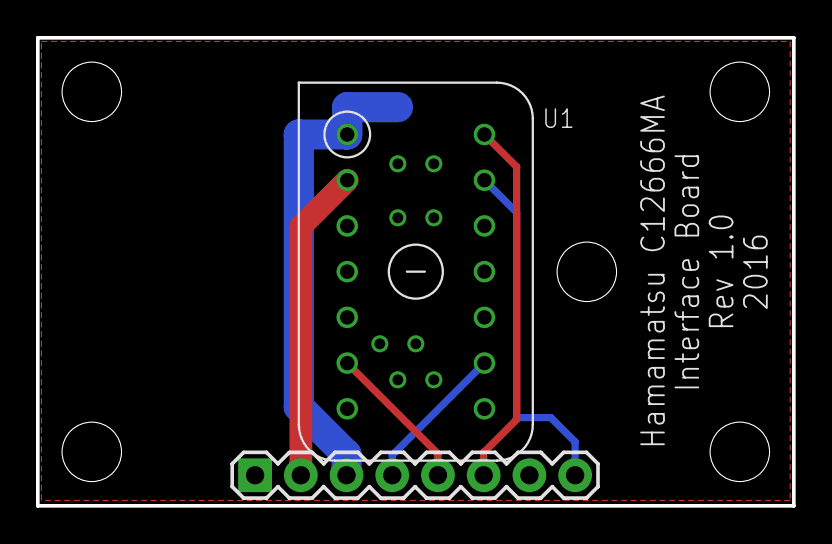
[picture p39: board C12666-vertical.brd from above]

Board: 2 copper layers, 42.0 x 26.0 mm, 8 parts (1 on the bottom side), 7 nets.

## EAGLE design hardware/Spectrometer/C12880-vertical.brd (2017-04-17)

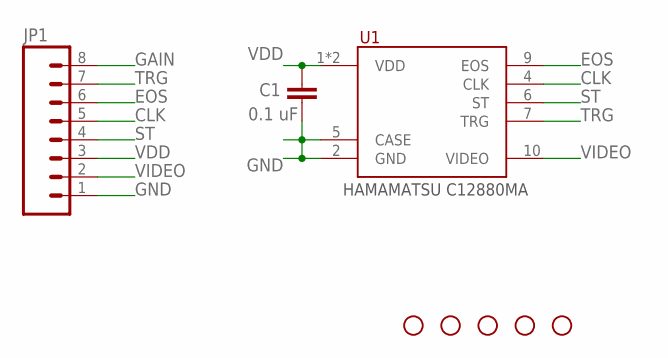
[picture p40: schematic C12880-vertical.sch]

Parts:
C1: 0.1 uF; C0805
JP1: M08SILK_FEMALE_PTH; 1X08
STANDOFF1, STANDOFF2, STANDOFF3, STANDOFF4, STANDOFF5: STAND-OFF
U1: MICROSPEC-C12880MA; C12880MA

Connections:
CLK: JP1.5, U1.4 (CLK)
EOS: JP1.6, U1.9 (EOS)
GAIN: JP1.8
GND: C1.2, JP1.1, U1.2 (GND), U1.5 (CASE)
ST: JP1.4, U1.6 (ST)
TRG: JP1.7, U1.7 (TRG)
VDD: C1.1, JP1.3, U1.1 (VDD), U1.3 (VDD)
VIDEO: JP1.2, U1.10 (VIDEO)

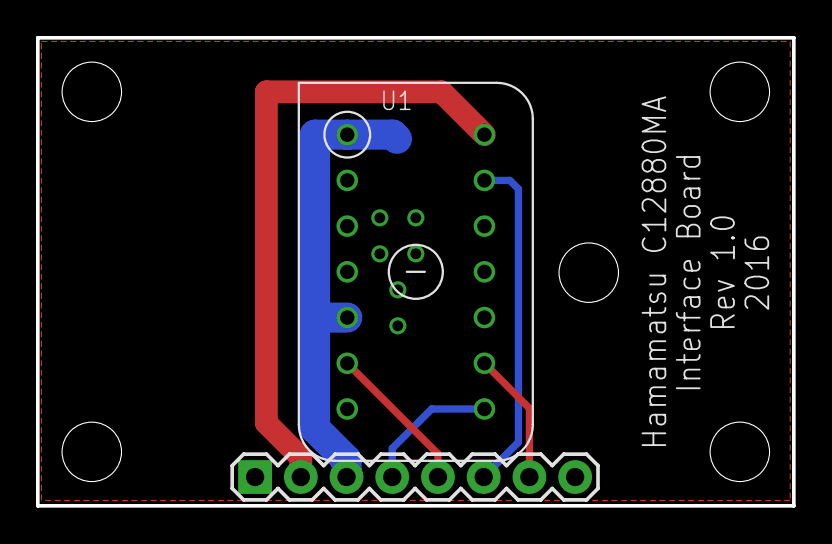
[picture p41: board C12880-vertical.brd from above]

Board: 2 copper layers, 42.0 x 26.0 mm, 8 parts (1 on the bottom side), 7 nets.

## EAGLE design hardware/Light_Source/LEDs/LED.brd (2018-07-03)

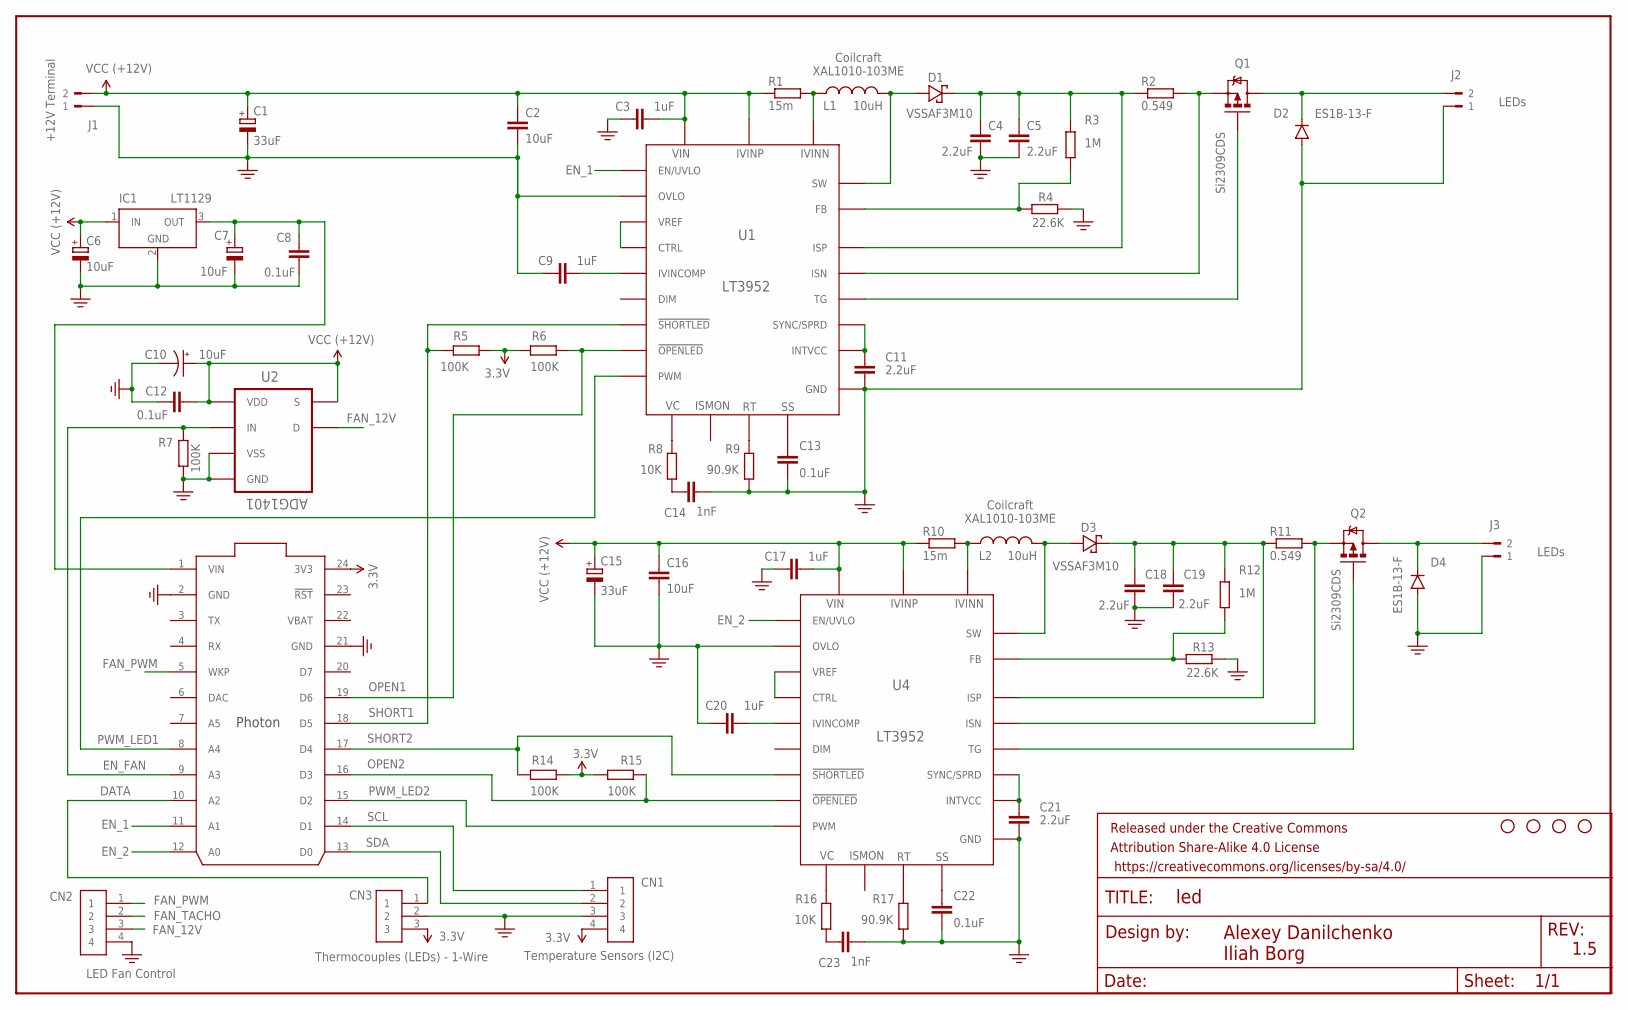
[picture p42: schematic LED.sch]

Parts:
C1, C15: 33uF; PANASONIC_E
C2, C16: 10uF; C1206
C3, C9, C17, C20: 1uF; C0805
C4, C5, C18, C19: 2.2uF; C1206
C6, C7: 10uF; CT7343
C8, C12, C13, C22: 0.1uF; C0805
C10: 10uF; EIA3216
C11, C21: 2.2uF; C0805
C14, C23: 1nF; C0805
CN1: Temperature Sensors (I2C); 1X04-BIG
CN2: LED Fan Control; 1X04-BIG
CN3: Thermocouples (LEDs) - 1-Wire; 1X03
D1, D3: VSSAF3M10; SODFL5226X100N
D2, D4: ES1B-13-F; SMA-DIODE_ALT
FRAME1: 1.0; CREATIVE_COMMONS
IC1: LT1129; SOT223
J1: +12V Terminal; WEIDMULLER_PM5.08_2
J2, J3: LEDs; WEIDMULLER_PM5.08_2
L1, L2: 10uH; XAL1010
Q1, Q2: Si2309CDS; SOT23-3
R1, R10: 15m; R1206
R2, R11: 0.549; R1206
R3, R12: 1M; R0805
R4, R13: 22.6K; R0805
R5, R6, R7, R14, R15: 100K; R0805
R8, R16: 10K; R0805
R9, R17: 90.9K; R0805
STANDOFF1, STANDOFF2, STANDOFF3, STANDOFF4: STAND-OFF
U1, U4: LT3952; TSSOP-28_FE/EB-M
U2: ADG1401; SOP65P490X110-8N
U3: PHOTON_WITH_HEADERS; PHOTON

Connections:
3.3V: CN1.4, CN3.3, R5.1, R6.2, R14.2, R15.1, U3.24 (3V3)
+5VDC: C7.+, C8.1, IC1.3 (OUT), U3.1 (VIN)
DATA: CN3.1, U3.10 (A2)
EN_1: U1.8 (EN/UVLO), U3.11 (A1)
EN_2: U3.12 (A0), U4.8 (EN/UVLO)
EN_FAN: R7.2, U2.6 (IN), U3.9 (A3)
FAN_12V: CN2.3, U2.8 (D)
FAN_PWM: CN2.1, U3.5 (WKP)
FAN_TACHO: CN2.2
GND: C1.-, C2.2, C3.2, C4.2, C5.2, C6.-, C7.-, C8.2, C9.2, C10.C (-), C11.2, C12.1, C13.2, C14.2, C15.-, C16.2, C17.2, C18.2, C19.2, C20.2, C21.2, C22.2, C23.2, CN1.3, CN2.4, CN3.2, D2.A, D4.A, IC1.2 (GND), IC1.4 (GND), J1.1, J2.1, J3.1, R4.1, R7.1, R9.1, R13.1, R17.1, U1.1 (GND), U1.9 (OVLO), U1.12 (GND), U1.28 (GND), U1.EPAD (GND), U2.3 (GND), U2.7 (VSS), U3.2 (GND), U3.21 (GND), U4.1 (GND), U4.9 (OVLO), U4.12 (GND), U4.28 (GND), U4.EPAD (GND)
unnamed: L1.1, R1.2, U1.5 (IVINN)
unnamed: D1.2 (A), L1.2, U1.2 (SW), U1.3 (SW), U1.4 (SW)
unnamed: C4.1, C5.1, D1.1 (K), R2.1, R3.2, U1.27 (ISP)
unnamed: R3.1, R4.2, U1.16 (FB)
unnamed: D2.C, J2.2, Q1.3 (D)
unnamed: Q1.2 (S), R2.2, U1.26 (ISN)
unnamed: Q1.1 (G), U1.25 (TG)
unnamed: C11.1, U1.10 (INTVCC), U1.11 (SYNC/SPRD)
unnamed: U1.17 (CTRL), U1.18 (VREF)
unnamed: C9.1, U1.23 (IVINCOMP)
unnamed: R9.2, U1.14 (RT)
unnamed: C13.1, U1.19 (SS)
unnamed: C14.1, R8.1
unnamed: R8.2, U1.13 (VC)
unnamed: L2.1, R10.2, U4.5 (IVINN)
unnamed: D3.2 (A), L2.2, U4.2 (SW), U4.3 (SW), U4.4 (SW)
unnamed: C18.1, C19.1, D3.1 (K), R11.1, R12.2, U4.27 (ISP)
unnamed: D4.C, J3.2, Q2.3 (D)
unnamed: Q2.2 (S), R11.2, U4.26 (ISN)
unnamed: R12.1, R13.2, U4.16 (FB)
unnamed: Q2.1 (G), U4.25 (TG)
unnamed: C21.1, U4.10 (INTVCC), U4.11 (SYNC/SPRD)
unnamed: U4.17 (CTRL), U4.18 (VREF)
unnamed: C20.1, U4.23 (IVINCOMP)
unnamed: C22.1, U4.19 (SS)
unnamed: R17.2, U4.14 (RT)
unnamed: C23.1, R16.1
unnamed: R16.2, U4.13 (VC)
OPEN1: R6.1, U1.22 (!OPENLED), U3.19 (D6)
OPEN2: R15.2, U3.16 (D3), U4.22 (!OPENLED)
PWM_LED1: U1.20 (PWM), U3.8 (A4)
PWM_LED2: U3.15 (D2), U4.20 (PWM)
SCL: CN1.1, U3.14 (D1)
SDA: CN1.2, U3.13 (D0)
SHORT1: R5.2, U1.21 (!SHORTLED), U3.18 (D5)
SHORT2: R14.1, U3.17 (D4), U4.21 (!SHORTLED)
VBAT: U3.22 (VBAT)
VDD: C1.+, C2.1, C3.1, C6.+, C10.A (+), C12.2, C15.+, C16.1, C17.1, IC1.1 (IN), J1.2, R1.1, R10.1, U1.6 (IVINP), U1.7 (VIN), U2.1 (S), U2.4 (VDD), U4.6 (IVINP), U4.7 (VIN)

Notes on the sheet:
1.5
Coilcraft XAL1010-103ME

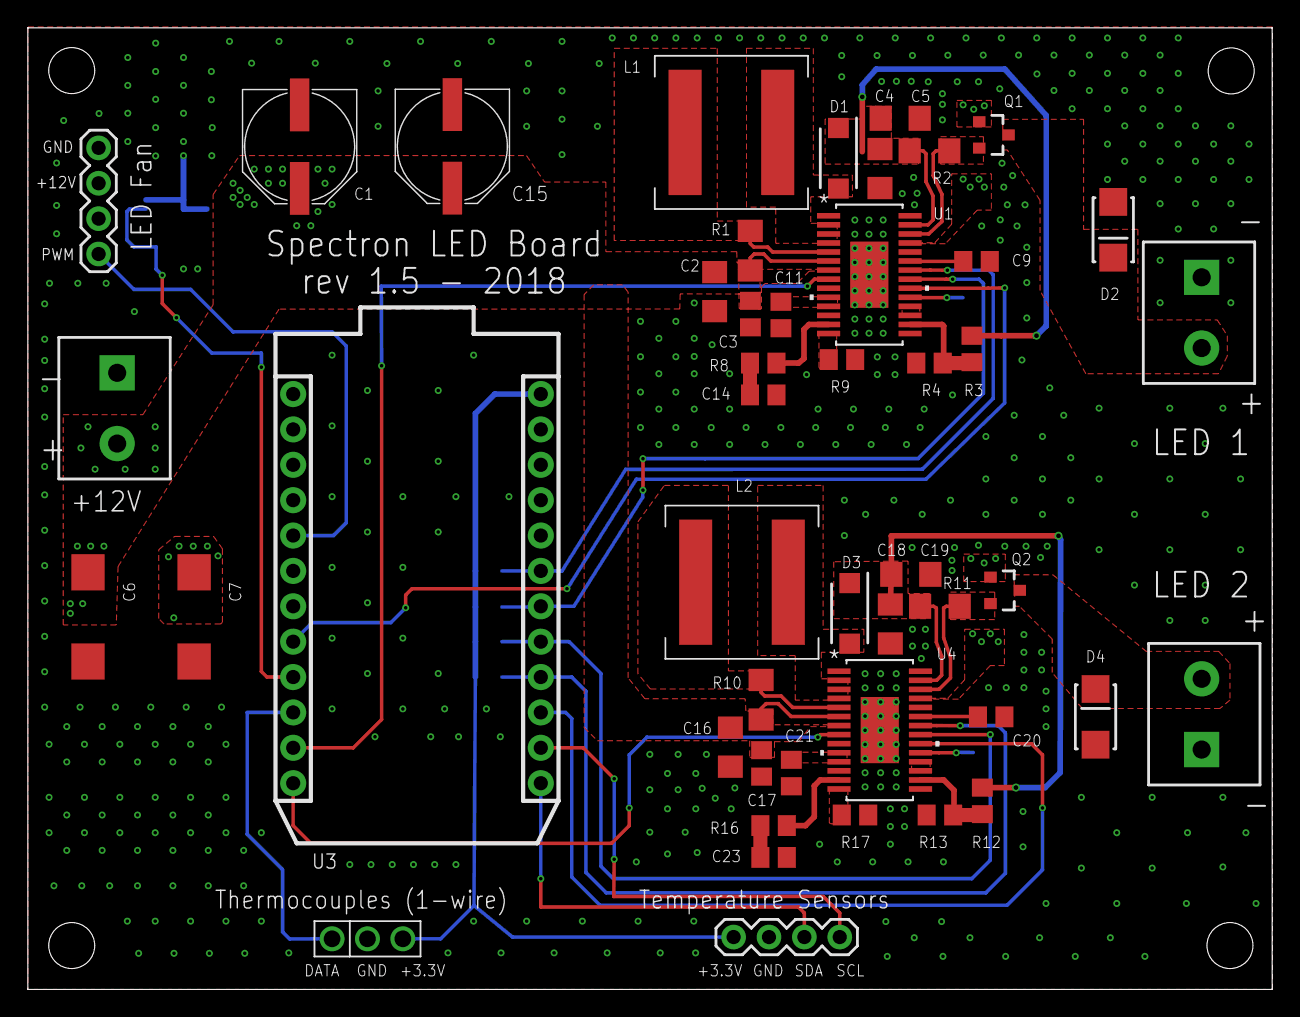
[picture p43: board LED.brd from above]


Board: 2 copper layers, 89.3 x 69.0 mm, 64 parts (12 on the bottom side), 46 nets.

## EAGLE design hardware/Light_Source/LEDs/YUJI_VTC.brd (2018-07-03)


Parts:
CN1: JST_4PIN; JSTPH4
LD1: YUJI_COB_13X4CUTOUT; YUJI_COB_13X4_CUTOUT
STANDOFF1, STANDOFF2, STANDOFF3, STANDOFF4: STAND-OFF

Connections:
unnamed: CN1.3, LD1.ANODE1
unnamed: CN1.4, LD1.CATHODE1
unnamed: CN1.1, LD1.CATHODE2
unnamed: CN1.2, LD1.ANODE2


Board: 2 copper layers, 98.0 x 74.0 mm, 6 parts (0 on the bottom side), 4 nets.

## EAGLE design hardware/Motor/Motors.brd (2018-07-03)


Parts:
C1: 0.022 uF; C0805
C2: 0.22 uF; C0805
C3, C4: 0.47 uF; C0805
C5, C6: 0.01 uF; C0805
C7: 100uF; CT7343
C8: 47 uF; CT7343
C9: 47uF; CT7343
C10: 0.1 uF; C0805
C11: 0.1uF; C0805
D1: PMEG2010ER; SOD123
FRAME1: FRAME-LETTER; CREATIVE_COMMONS
IC1: MC33269ST; SOT223
J1: +12V; WEIDMULLER_PM5.08_2
JP1: Stepper Connector; 1X04
JP2: X1/X4 Jumper; 1X03
JP3: Rotary Connector; 1X04
Q1, Q2: BSS138; SOT23-3
R1: 5K; R0805
R2: 100 K; R0805
R3, R4, R5, R6: 10K; R0805
R7: 30K; R0805
STANDOFF1, STANDOFF2, STANDOFF3, STANDOFF4: STAND-OFF
U1: DRV8884PWPR; SOP65P640X120-29N
U2: PHOTON_WITH_HEADERS; PHOTON
U3: LS7083N-S; SOIC127P600X175-8N

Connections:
+3.3V: Q1.1 (G), Q2.1 (G), R1.1, R5.1, R6.1, U2.24 (3V3)
+5V: C9.+, C10.1, C11.2, D1.A, IC1.2 (OUT), IC1.4 (OUT), JP2.1, JP3.4, R3.1, R4.1, U3.2 (VDD)
DECAY: U1.24 (DECAY), U2.6 (DAC)
DNCK_3V: Q2.2 (S), R6.2, U2.13 (D0)
DNCK_5V: Q2.3 (D), R4.2, U3.7 (DNCK)
GND: C3.2, C4.2, C5.2, C6.2, C7.-, C8.-, C9.-, C10.2, C11.1, IC1.1 (GND/ADJ), J1.1, JP2.3, JP3.1, R2.2, U1.6 (PGND), U1.9 (PGND), U1.12 (GND), U1.25 (GND), U2.2 (GND), U2.21 (GND), U3.3 (VSS)
unnamed: U1.18 (ENABLE), U2.11 (A1)
unnamed: C2.2, U1.3 (VCP)
unnamed: C1.1, U1.2 (CPH)
unnamed: C1.2, U1.1 (CPL)
unnamed: U1.22 (M1), U2.5 (WKP)
unnamed: U1.17 (NSLEEP), U2.12 (A0)
unnamed: R7.1, U1.16 (PREF)
unnamed: C4.1, U1.13 (AVDD)
unnamed: C3.1, U1.14 (DVDD)
unnamed: D1.C, U2.1 (VIN)
unnamed: U1.19 (STEP), U2.10 (A2)
unnamed: U1.20 (DIR), U2.8 (A4)
unnamed: U1.21 (M0), U2.7 (A5)
unnamed: U1.23 (TRQ), U2.4 (RX)
unnamed: R7.2, U2.9 (A3)
unnamed: R2.1, U3.1 (RBIAS)
unnamed: JP1.1, U1.5 (AOUT1)
unnamed: JP1.2, U1.7 (AOUT2)
unnamed: JP2.2, U3.6 (X4_X1)
unnamed: JP1.3, U1.8 (BOUT2)
unnamed: JP1.4, U1.10 (BOUT1)
NFAULT: R1.2, U1.15 (NFAULT), U2.15 (D2)
ROTARY_A: JP3.3, U3.4 (A)
ROTARY_B: JP3.2, U3.5 (B)
UPCK_3V: Q1.2 (S), R5.2, U2.14 (D1)
UPCK_5V: Q1.3 (D), R3.2, U3.8 (UPCK)
VBAT: U2.22 (VBAT)
VIN: C2.1, C5.1, C6.1, C7.+, C8.+, IC1.3 (IN), J1.2, U1.4 (VM), U1.11 (VM)

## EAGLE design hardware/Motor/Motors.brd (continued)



Board: 2 copper layers, 59.0 x 48.0 mm, 34 parts (8 on the bottom side), 33 nets.

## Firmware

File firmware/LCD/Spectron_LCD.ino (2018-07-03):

/*
 *  Spectron_LCD.ino - Demo application of the Spectron board capabilities  
 *                     with Adafruit ILI9340 TFT screen displaying measured 
 *                     spectrum. This is not actively maintained.
 *
 *  Copyright 2015-2017 Alexey Danilchenko
 *
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
 *  You should have received a copy of the GNU General Public License
 *  along with this program; if not, write to the Free Software
 *  Foundation, 51 Franklin Street - Fifth Floor, Boston,
 *  MA 02110-1301, USA.
 */

SYSTEM_MODE(MANUAL);

#include "C12666MA.h"
#include "Adafruit_ILI9340.h"

#define ADC_REF_SEL_1  A1
#define ADC_REF_SEL_2  A0
#define ADC_CNV        DAC
#define SPI_SS_1       WKP
#define D_PWM          RX
#define SPI_SS_2       A2
#define SPI_MOSI       A5
#define SPI_MISO       A4
#define SPI_SCK        A3
#define SDA            D0
#define SCL            D1

#define TRG_IN         A2   // extrenal trigger button
#define TRG_FLASH      TX
#define TRG_CAMERA     D2

#define TRG_3V         D3
#define EOS_3V         D4
#define CLK_3V         D5
#define ST_3V          D6
#define GAIN_3V        D7

#define LCD_DC        SDA
#define LCD_RESET     SCL
#define LCD_SD_CS     SPI_SS_2
#define LCD_CS        SPI_SS_1
#define LCD_MOSI      SPI_MOSI
#define LCD_MISO      SPI_MISO
#define LCD_SCK       SPI_SCK
#define LCD_BACKLIGHT D_PWM

#define INACTIVE_DELAY_MS 120000

// calibration data for my sensor 15F00163
const float CALIBRATION_15F00163[] =
    {323.3668711, 2.384682045, -5.995865297E-4, -8.602293347E-6, 1.840343099E-8, -1.424592223E-11};

// spectrometer object - can be only one per application
C12666MA spec(TRG_3V,
              EOS_3V,
              GAIN_3V,
              CLK_3V,
              ST_3V,
              TRG_CAMERA,
              ADC_REF_SEL_1,
              ADC_REF_SEL_2,
              ADC_CNV,
              CALIBRATION_15F00163);

// TFT screen object
Adafruit_ILI9340 tft(LCD_SD_CS,
                     LCD_DC,
                     LCD_RESET);

// Wavelength indexes for screen 400,450,500,550,600,650,700,750
#define WV_LABELS      10
#define WV_LABEL_START 350
#define WV_LABEL_STEP  50
uint16_t wvLabelIndex[WV_LABELS];

// indicator if black was measured
bool blackMeasured = true;

// last active time
unsigned long lastActive = 0;

// draw the main screen
void drawScreen()
{
    tft.3Init();
    tft.fillScreen(ILI9340_BLACK);
    tft.setRotation(3);    // orientation landscape

    // draw header
    tft.setCursor(0, 0);
    tft.setTextColor(ILI9340_WHITE);
    tft.setTextSize(1);
    tft.print("Peak: ");
    tft.print(spec.getPeakWavelength(), 2);
    tft.print("nm    Max: ");
    tft.print(spec.getPeakValue());
    tft.print("    Black: ");
    tft.print(spec.getMaxBlack());

    // draw axis
    uint16_t g_x = 0, g_y = 10, g_w = 320, g_h = 220;
    uint16_t color = ILI9340_WHITE;
    tft.drawFastHLine(0, g_y+g_h, g_w, color);
    uint16_t lblWavelength = WV_LABEL_START;
    for (int i=0; i<WV_LABELS; i++)
    {
        if (wvLabelIndex[i] == SPEC_PIXELS)
            break;
        uint16_t l_x = g_x + (wvLabelIndex[i] * g_w / SPEC_PIXELS);
        tft.drawFastVLine(l_x, g_y+g_h-1, 3, color);
        tft.setCursor(l_x - 8, g_y+g_h+2);
        tft.print(lblWavelength);
        lblWavelength += WV_LABEL_STEP;
    }

    // draw the maxvoltage
    // draw spectrum
    if (spec.hasMeasuredData())
    {
        uint16_t x0 = g_x;
        uint16_t y0 = g_y + g_h - (((uint32_t)g_h*spec.getMeasurement(0) + 16383) /16384);
        for (int i=1; i<SPEC_PIXELS; i++)
        {
            uint16_t x1 = g_x + ((i * g_w + SPEC_PIXELS - 1) / SPEC_PIXELS);
            uint16_t y1 = g_y + g_h - (((uint32_t)g_h*spec.getMeasurement(i) + 16383) /16384);
            tft.drawLine(x0, y0, x1, y1, ILI9340_YELLOW);
            x0 = x1;
            y0 = y1;
        }
    }
    else if (!blackMeasured)
    {
        tft.setTextSize(2);
        tft.setCursor(g_x, g_y + (g_h>>1)- 32);
        tft.setTextColor(ILI9340_RED);
        tft.println("    Cover the sensor and");
        tft.println("  trigger black reference");
        tft.println("       measurement");
    }
}

// main firmware initialisation
void setup()
{
    pinMode(LCD_BACKLIGHT, OUTPUT);
    pinMode(LCD_CS,        OUTPUT);
    pinMode(LCD_SD_CS,     OUTPUT);
    pinMode(LCD_DC,        OUTPUT);
    pinMode(LCD_RESET,     OUTPUT);

    pinMode(TRG_IN,     INPUT_PULLUP);
    pinMode(TRG_CAMERA, OUTPUT);
    pinMode(TRG_FLASH,  OUTPUT);

    // reset everything
    pinResetFast(LCD_CS);
    pinResetFast(LCD_SD_CS);
    pinResetFast(LCD_DC);
    pinResetFast(LCD_RESET);


    // initialise spectrometer
    spec.begin();
    spec.setIntTime(500);   // 0.5s to start with
    spec.setAdcReference(ADC_4V);

    // get the wavelength label indexes
    uint16_t idx = 0;
    for (int i=0; i<WV_LABELS; i++)
    {
        uint16_t lblWavelength = WV_LABEL_START + (i * WV_LABEL_STEP);
        while (idx < SPEC_PIXELS &&
               lblWavelength > spec.getWavelength(idx))
               ++idx;
        if (idx < SPEC_PIXELS)
            wvLabelIndex[i] = idx;
        else
            wvLabelIndex[i] = SPEC_PIXELS;
    }

    // enable TFT backlight
    pinSetFast(LCD_BACKLIGHT);
    tft.begin();

    // paint the screen
    drawScreen();

    lastActive = millis();
}

// Main event loop:
//     - Wait for trigger button press
//     - Start spectometer measurement and trigger camera/flash
//     - Display the results on TFT
//     - Store results on SD card
void loop(void)
{
    // poll the trigger button
    if (pinReadFast(TRG_IN) == LOW)
    {
        // debounce check
        delay(100);
        if (pinReadFast(TRG_IN) == LOW)
        {
            pinSetFast(LCD_BACKLIGHT);
            lastActive = millis();
            
            // initiate measurement
            spec.takeMeasurement();

            // paint the screen
            drawScreen();
        }
    }

    // check for inactivity
    if ((millis() - lastActive) > INACTIVE_DELAY_MS)
        pinResetFast(LCD_BACKLIGHT);

    // call for Spark process for manual system mode
    if (Particle.connected())
        Particle.process();
    else
        Particle.connect();
 }

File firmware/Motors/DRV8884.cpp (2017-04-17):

/*
 *  DRV8884.cpp - Texas Instruments DRV8884 driver for Motor board.
 *                This controls stepper motor and rotary encoder.
 *                Rotary encoder bit is supposed to be used as
 *                confirmaion mechanism for stepper motor position.
 *                At this point only basic readings of rotary
 *                encoder are developed - no confirmation code is
 *                implemented.
 *
 *  Copyright 2017 Alexey Danilchenko, Iliah Borg
 *
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
 *  You should have received a copy of the GNU General Public License
 *  along with this program; if not, write to the Free Software
 *  Foundation, 51 Franklin Street - Fifth Floor, Boston,
 *  MA 02110-1301, USA.
 */

#include "DRV8884.h"

// EEPROM addresses
#define EEPROM_CUR_POS_ADDR         0
#define EEPROM_MIN_POS_ADDR         4
#define EEPROM_MAX_POS_ADDR         8
#define EEPROM_ROTARY_ADDR          12
#define EEPROM_DECAY_ADDR           16
#define EEPROM_TIMER_PER_ADDR       20
#define EEPROM_TRQ_ADDR             24
#define EEPROM_STEP_ADDR            28
#define EEPROM_STEPS_PER_POS_ADDR   32

#define EEPROM_FREE_ADDR            36  // free address for application usage

//
// Timer prescaler - this is what CPU counter clock frequency is divided by to get the frequency
//      generally prescaler is calculated as SYSCORECLOCK (60000000 for Photon for base timers)
//      divided by the frequency of the timer counter. For example:
//
//      TIMER_PRESCALER = (SYSCORECLOCK / 1000000) - 1 to get TIM counter clock = 1MHz
//
#define  TIMER_PRESCALER     599       // for basic timers at 60MHz it gives 10us timer unit counter
#define  TIMER_UNITS_PER_SEC 100000UL  // number of timer units per sec for the above prescaler
#define  MIN_TIMER_PERIOD    10        // min timer tick - in above 10us units it will trigger every 0.1ms
#define  MAX_TIMER_PERIOD    50000     // max timer tick - in above 10us units it will trigger every 500ms
uint32_t TIMER_PERIOD_CNT =  1000;     // in above 10us units it will trigger every 10ms

// State machine
enum state_t {
    STATE_RUN,
    STATE_STOP
};

// driver state variables
static volatile state_t drvState      = STATE_STOP;
static bool             drvCLK        = LOW;
static int32_t          drvPulsesCount  = 0;
static volatile bool    timerOn       = false;
static volatile int32_t rotaryCounter = false;

// Driver pins
uint8_t drvPinCLK  = NO_PIN;

// Decay DAC values
static const int decayDAC[] = {
    0,      // DECAY_SLOW_MIXED
    373,    // DECAY_MIXED_30_PERCENT, 300mV for 3.3V, 12 bit DAC
    1241,   // DECAY_MIXED_60_PERCENT, 1V for 3.3V, 12 bit DAC
    3723    // DECAY_SLOW, 3V for 3.3V, 12 bit DAC
};

// Full step multipliers
static const int fullStepMultiplier[] = {
    1,      // STEP_FULL
    16,     // STEP_SIXTEENTH
    8,      // STEP_EIGHTS
    1,      // none - not used
    2,      // STEP_HALF
    4,      // STEP_QUARTER
    2       // STEP_HALF_NON_CIRCULAR
};

// ----------------------------------------------------
//   Timer clock and pins interrupt handling routines
// ----------------------------------------------------
void rotaryUp(void)
{
    ++rotaryCounter;
}

void rotaryDown(void)
{
    --rotaryCounter;
}

void drvClockInterrupt(void)
{
    if (TIM_GetITStatus(TIM7, TIM_IT_Update) != RESET)
    {
        TIM_ClearITPendingBit(TIM7, TIM_IT_Update);

        digitalWriteFast(drvPinCLK, drvCLK);

        switch (drvState) {
            case STATE_RUN:
                --drvPulsesCount;
                if (drvPulsesCount <= 0) {
                    drvPulsesCount = 0;
                    drvState = STATE_STOP;
                    drvCLK = LOW;
                }
                else
                    drvCLK = (drvCLK == HIGH) ? LOW : HIGH;
                break;


            case STATE_STOP:
            default:
                break;
        }
    }
}

// start active timer
void startDrvTimer(int32_t pulses)
{
    TIM_TimeBaseInitTypeDef timerInit = {0};
    NVIC_InitTypeDef nvicInit = {0};

    // set in timer guard
    if (timerOn)
        return;

    timerOn = true;

    // init state
    drvPulsesCount = pulses;
    drvState = STATE_RUN;

    // next value of CLK
    drvCLK = HIGH;

    // enable TIM7 clock
    RCC_APB1PeriphClockCmd(RCC_APB1Periph_TIM7, ENABLE);

    // enable timer IRQ
    nvicInit.NVIC_IRQChannel                   = TIM7_IRQn;
    nvicInit.NVIC_IRQChannelPreemptionPriority = 3;
    nvicInit.NVIC_IRQChannelSubPriority        = 0;
    nvicInit.NVIC_IRQChannelCmd                = ENABLE;
    NVIC_Init(&nvicInit);

    // setup timer
    timerInit.TIM_Prescaler         = TIMER_PRESCALER;
    timerInit.TIM_CounterMode       = TIM_CounterMode_Up;
    timerInit.TIM_Period            = TIMER_PERIOD_CNT;
    timerInit.TIM_ClockDivision     = TIM_CKD_DIV1;
    timerInit.TIM_RepetitionCounter = 0;

    // enable timer
    TIM_TimeBaseInit(TIM7, &timerInit);
    TIM_ITConfig(TIM7, TIM_IT_Update, ENABLE);
    TIM_Cmd(TIM7, ENABLE);
}

// stop active timer
void stopDrvTimer()
{
    NVIC_InitTypeDef nvicInit = {0};

    // disable timer
    TIM_Cmd(TIM7, DISABLE);

    // disable timer IRQ
    nvicInit.NVIC_IRQChannel    = TIM7_IRQn;
    nvicInit.NVIC_IRQChannelCmd = DISABLE;
    NVIC_Init(&nvicInit);

    // disable timer peripheral
    TIM_DeInit(TIM7);

    // reset pin
    pinResetFast(drvPinCLK);

    timerOn = false;
}

// Constructor/destructor
DRV8884::DRV8884(uint8_t nfault, uint8_t decay, uint8_t trq, uint8_t m0, uint8_t m1,
                 uint8_t dir, uint8_t step, uint8_t enable, uint8_t nsleep, uint8_t pref,
                 uint8_t up_clk, uint8_t down_clk)
{
    pinNfault_  = nfault;
    pinDecay_   = decay;
    pinTRQ_     = trq;
    pinM0_      = m0;
    pinM1_      = m1;
    pinDir_     = dir;
    pinStep_    = step;
    pinEnable_  = enable;
    pinNsleep_  = nsleep;
    pinPREF_    = pref;
    pinUpCLK_   = up_clk;
    pinDownCLK_ = down_clk;
    drvState    = STATE_STOP;
    drvCLK      = LOW;

    drvPinCLK     = pinStep_;
    isRunning_    = false;
    decayMode_    = DECAY_SLOW_MIXED;
    torqueMode_   = TORQUE_FULL;
    steppingMode_ = STEP_FULL;
    direction_    = DIR_FORWARD;

    // read position details from EPROM
    EEPROM.get(EEPROM_CUR_POS_ADDR, curPos_);
    if (curPos_ == 0xFFFFFFFF)
        // EEPROM was empty
        curPos_ = 0;

    EEPROM.get(EEPROM_MIN_POS_ADDR, minPos_);
    if (minPos_ == 0xFFFFFFFF)
        // EEPROM was empty
        minPos_ = 0;

    EEPROM.get(EEPROM_MAX_POS_ADDR, maxPos_);
    if (maxPos_ == 0xFFFFFFFF)
        // EEPROM was empty
        maxPos_ = 0;

    EEPROM.get(EEPROM_ROTARY_ADDR, rotaryCounter_);
    if (rotaryCounter_ == 0xFFFFFFFF)
        // EEPROM was empty
        rotaryCounter_ = curPos_;

    EEPROM.get(EEPROM_DECAY_ADDR, decayMode_);
    if (decayMode_ < 0  || decayMode_ > 3)
        // EEPROM was empty
        decayMode_ = DECAY_SLOW_MIXED;

    EEPROM.get(EEPROM_TIMER_PER_ADDR, stepsPerSec_);
    if (stepsPerSec_ == 0xFFFFFFFF)
        // EEPROM was empty
        setRotationSpeed(50);
    else
        setRotationSpeed(stepsPerSec_, false);

    EEPROM.get(EEPROM_TRQ_ADDR, torqueMode_);
    if (torqueMode_ == 0xFFFFFFFF)
        // EEPROM was empty
        torqueMode_ = TORQUE_FULL;

    EEPROM.get(EEPROM_STEP_ADDR, steppingMode_);
    if (steppingMode_ == 0xFFFFFFFF)
        // EEPROM was empty
        steppingMode_ = STEP_FULL;

    EEPROM.get(EEPROM_STEPS_PER_POS_ADDR, fullStepsPerPos_);
    if (fullStepsPerPos_ == 0xFFFFFFFF)
        // EEPROM was empty
        fullStepsPerPos_ = 1;
}

DRV8884::~DRV8884()
{
}

// Setup methods and setters
void DRV8884::begin()
{
    pinMode(pinDecay_,  OUTPUT);
    pinMode(pinTRQ_,    OUTPUT);
    pinMode(pinM0_,     OUTPUT);
    pinMode(pinM1_,     OUTPUT);
    pinMode(pinDir_,    OUTPUT);
    pinMode(pinStep_,   OUTPUT);
    pinMode(pinEnable_, OUTPUT);
    pinMode(pinNsleep_, OUTPUT);
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

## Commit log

2017-04-17 Initial submisssion
    Submission of well tested hardware, firmware. Software is being developed and will follow later.
    [C12666-vertical.brd, C12666-vertical.sch, C12666.brd, C12666.sch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]
2018-07-03 Cumulative changes: adding light sources, boards, firmwares, construction details
    [C12666-vertical.brd, C12666-vertical.sch, C12666.brd, C12666.sch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]
2018-12-01 Spectrometer firmwares and sample application for Windows
    Spectrometer firmwares rewritten to provide automatic measurements, calibration and afew other features. Sample Windows application is provided to operate Spectron spectrometer board and measure spec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
2019-04-13 Update 1.2
    Firmware changes:
    - configurable spectral range
    - saturation and black level calibration
    - spectral response calibration and normalisation of measurements
    SpectrometerApp changes:
    - Spectrometer calibration page allowing calibration of various spectrometer properties
    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
2019-04-15 Minor fixes
    Fixed copy operator that prevented re-login to other devices
2021-12-15 Added Camera SRF application note

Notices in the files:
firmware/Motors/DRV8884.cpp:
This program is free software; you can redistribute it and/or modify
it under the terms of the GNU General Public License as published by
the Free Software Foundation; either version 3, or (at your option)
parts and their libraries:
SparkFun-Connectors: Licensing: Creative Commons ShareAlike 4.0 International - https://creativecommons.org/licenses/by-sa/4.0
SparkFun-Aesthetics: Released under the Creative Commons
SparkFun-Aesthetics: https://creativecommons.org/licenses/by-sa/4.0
